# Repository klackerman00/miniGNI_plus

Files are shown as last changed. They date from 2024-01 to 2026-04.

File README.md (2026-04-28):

# miniGNI+ - An update to the original miniGNI 
Welcome to the miniGNI+, an extension of the original [miniature giant nuclei impactor (mini-GNI)](https://github.com/nugentlab/miniGNI) created at the University of Hawai'i by the [Nugent Lab](http://alisonnugent.com/). This instrument utilizes the same methodology as the original miniGNI with an improved design that facilitates use. Additionally, we've included an in-situ anemometer. More information on the methods of the original instrument can be found in this paper: 

> A New Instrument for Determining the Coarse-Mode Sea Salt Aerosol Size Distribution - [Taing et al., 2021](https://journals.ametsoc.org/view/journals/atot/38/11/JTECH-D-20-0197.1.xml)

while the microscope methods are explained in this paper: 

> The Giant Nucleus Impactor (GNI)—A System for the Impaction and Automated Optical Sizing of Giant Aerosol Particles with Emphasis on Sea Salt. Part I: Basic Instrument and Algorithms - [Jensen et al., 2020](https://journals.ametsoc.org/view/journals/atot/37/9/jtechD190109.xml?rskey=7VVZ45&result=6)

Results using the observations gathered by the miniGNI V1.0 are in this corresponding paper: 

> Mechanisms controlling giant sea salt aerosol size distributions along a tropical orographic coastline - [Ackerman et al., 2023](https://acp.copernicus.org/articles/23/13735/2023/)

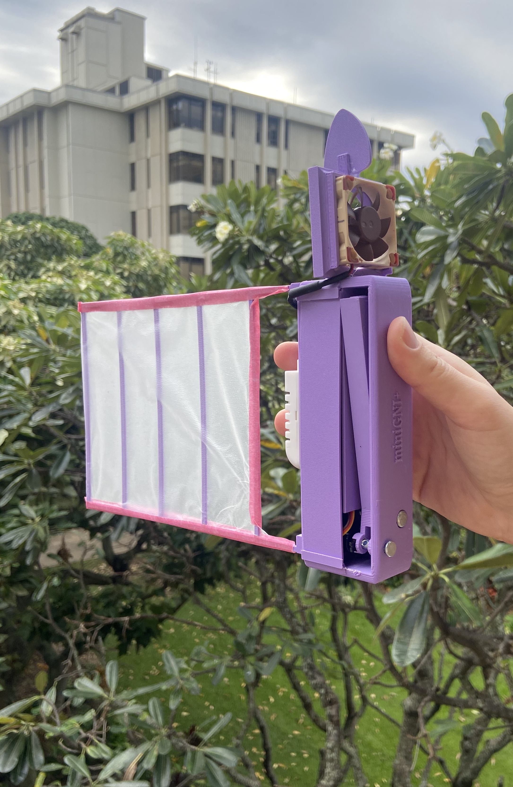
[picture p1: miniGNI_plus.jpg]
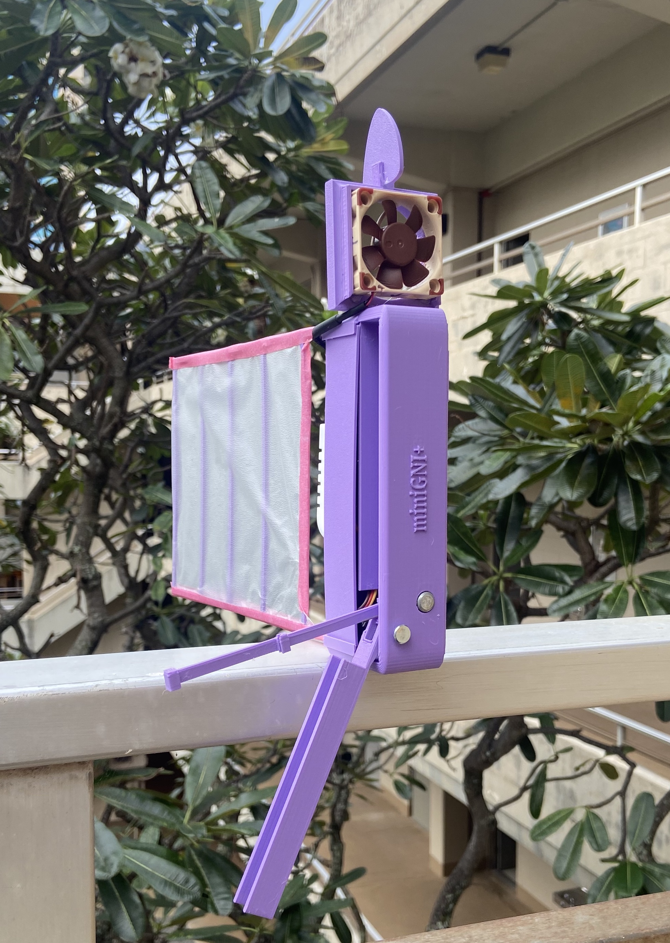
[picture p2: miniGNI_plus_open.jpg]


## Updates from the miniGNIv1.0 to the miniGNI+  
### The Door  
The door was removed from the miniGNIv1 to the miniGNI+ and replaced with an encapsulating cover. This cover offers minimal resistance against the micro-servo motor resulting in fewer failures of the door closure system (a common issue with version 1). For over 100 collected samples, the miniGNI+ closure system has never failed. Additionally, this new closure ensures no airflow around the polycarbonate slide during transport, offering increased protection from contamination over the prior model. 

### The RH Sensor
The relative humidity sensor of miniGNIv1 utilized Adafruits DHT22/2301 sensor but has been replaced with Adafruits 2301B. The 2301B sensor is practically the same, however, utilizes an I<sup>2</sup>C interface! This results in some minor changes to the wiring. 

### Detachable Wing
The wing of the miniGNI+ clips on for easy storage of the instruments. Several STL files are included at various lengths. 

### Anemometer
The largest upgrade to the miniGNI+ is the addition of an in-situ anemometer. A computer fan has been converted to an anemometer to allow for in-situ wind measurements, rather than utilizing a ground station with a wing power law conversion to calculate wind aloft. 

# In-situ Instrumentation: 
- Temperature (+/- 0.3 &deg;C)
- Relative Humidity (+/- 2%)
- Pressure/Altimetry (+/- 1.5 Pa, ~0.3 m)
- Wind Speed (+/- 0.5 m s<sup>-1</sup>)
- Sea Salt Aerosol Size Distribution 

### Optional Add-On
- Orientation (Euler Angles)

# Assembly

Gather the parts necessary for assembly. You'll need: 

### 3D Printed Parts: 
- Body (big purple body)
- Arm (small skinny)
- Anemometer house (square with circular cutout)

### Electronics: 
- Male to male pins; at least 16 continuous pieces long (less if you want to make your life harder)
- Feather M0 RFM9x LoRA radio sensor (with lipo battery and micro-usb ports)
- Adalogger Featherwing (with micro SD and CR1220 watch battery ports)
- Relative humidity sensor (black, Adafruit AM2301B)
- Altimeter (Adafruit, MPL3115A2)
- Resistor (Digikey, 10k ohm)
- Microserver motor (Adafruit, P169)
- MicroSD card
- Computer Fan (NF-A4x10 FLX Computer Fan) - [Reference to Leeman Geophysical, LLC](https://leemangeophysicalllc.github.io/mini-GNI/fan_mods.html)
- Wire for soldering parts together
- Antenna wire (specifically cut to 8.3 cm) 

### Hardware: 
- Clevis Pin (3/16 x 5/8 inches)
- Clevis Pin #2 (3/16 x 1 inch)
- Arm Spring (McMaster Carr)
- Wire for soldering together these parts
  
# Fritzing Diagram 
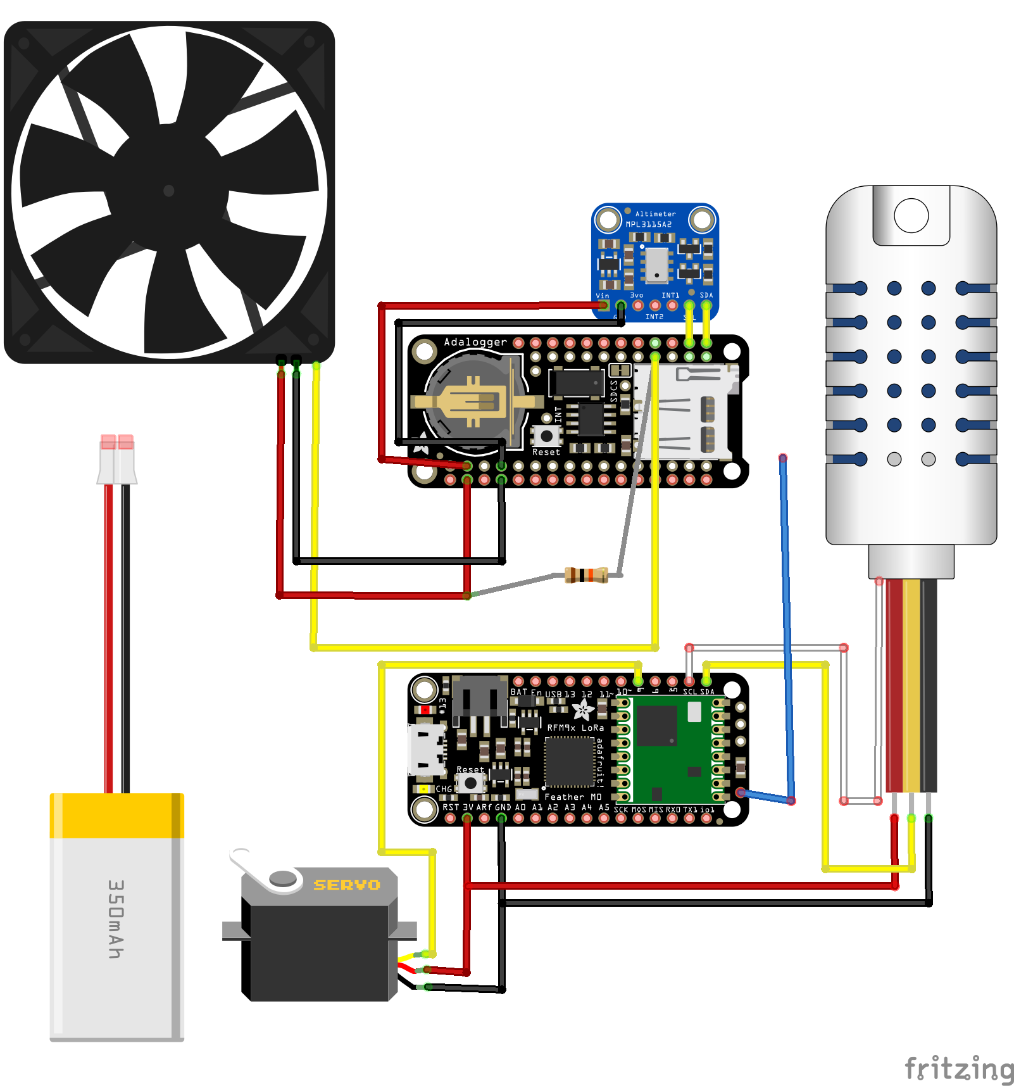
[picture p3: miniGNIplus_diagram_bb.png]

Connect the above parts using the following electrical diagram. 

# Base Station 
The base station can be made in accordance with the original base station found in [this document](https://github.com/nugentlab/miniGNI/blob/master/miniGNI_Assembly/DocumentingAssembly.docx) on the original miniGNI page. Ensure that the frequency set on your miniGNI+ and the matching base station are the same! 

# Arduino IDE Software Upload
We're currently on the V2 of the miniGNI+! Please use this updated source code that accounts for the change in relative humidity sensor from the original analog sensor to the new I2C sensor. Both code for the miniGNI and miniGNI base station are provided. 

We utilized some outdated versions of specific libraries (which we provide below). We cannot guarantee that these will work with updated libraries. 

### Libraries in use and version numbers: 
- Ethernet by Various (2.0.0)
- Firmata by Firmata (2.5.8)
- Keyboard by Arduino (1.0.2)
- LiquidCrystal by Arduino, Adafruit (1.0.7)
- Mouse by Arduino (1.0.1)
- SD by Arduino, SparkFun (1.2.4)
- Servo by Michael (1.1.7)
- Stepper by Arduino (1.1.3)
- Temboo by Temboo (1.2.1)
- Adafruit AHTX0 by Adafruit (2.0.5)
- Adafruit BNO055 by Adafruit (1.4.3)
- Adafruit BusIO by Adafruit (1.7.2)
- Adafruit Circuit Playground by Adafruit (1.10.4)
- Adafruit GFX Library by Adafruit (1.10.6)
- Adafruit ILI9341 by Adafruit (1.5.6)
- Adafruit MPL3115A2 by Adafruit (1.2.1)
- Adafruit STMPE610 by Adafruit (1.1.3)
- Adafruit TouchScreen by Adafruit (1.1.1)
- Adafruit Unified Sensor by Adafruit (1.1.4)
- DHT sensor Library by Adafruit (1.4.1)
- FIR filter by Leeman Geophysical LLC by Adafruit (0.1.1)
- RF24 by TMRh20 (1.3.11)
- RTClib by Adafruit (1.12.5)
- RadioHead by Mike McCauley (1.112)
- TinyWireM by Adafruit (1.1.0)
- Bridge by Arduino (1.7.0)
- Esplora by Arduino (1.0.4)
- GSM by Arduino (1.0.6)
- Robot Control by Arduino (1.0.4)
- Robot IR Remote by Arduino (2.0.0)
- Robot Motor by Arduino (1.0.3)
- SpacebrewYun by Julio Terra (1.0.2)
- TFT by Arduino, Adafruit (1.0.6)
- WiFI by Arduino (1.2.7)

### Specific Boards to Download: 
- Adafruit SAMD Boards (1.7.17)

This can be added by going to the Arduino IDE in the top right corner > Settings, and then adding this link to the "Additional Boards Manager URL" 
https://adafruit.github.io/arduino-board-index/package_adafruit_index.json

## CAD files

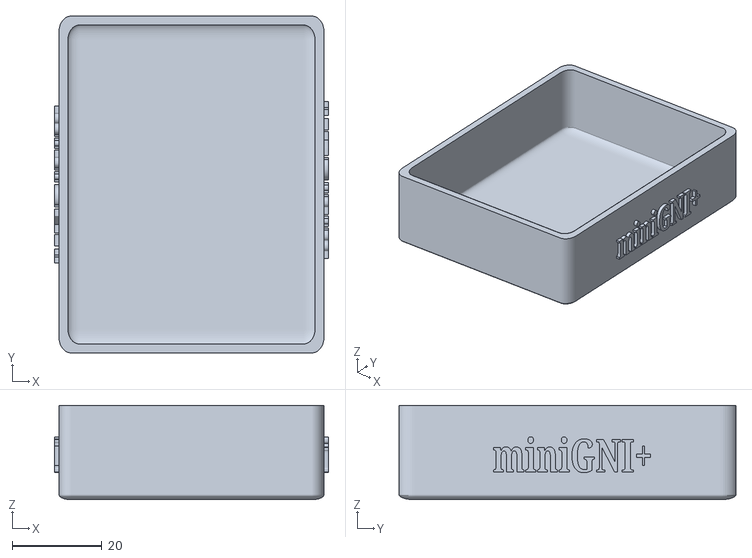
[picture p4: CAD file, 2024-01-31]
miniGNI_plus_V2/miniGNI_plus_V2_basestation_bottom.stl
61.0 x 75.0 x 21.0

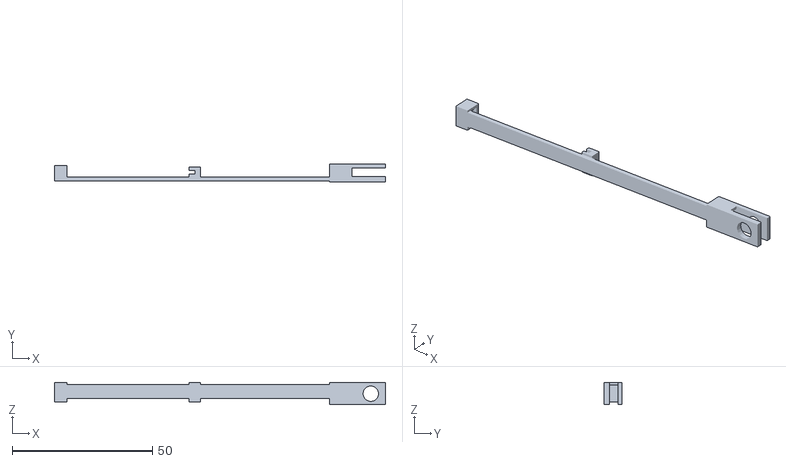
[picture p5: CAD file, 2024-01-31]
miniGNI_plus_V2/miniGNI_plus_V2_arm.stl
118.0 x 6.25 x 8.00

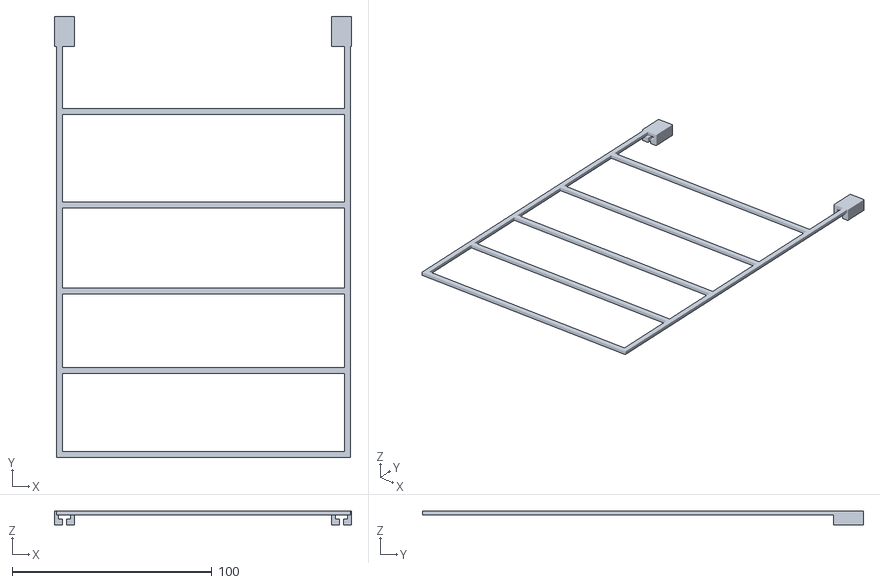
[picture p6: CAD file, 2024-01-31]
miniGNI_plus_V2/miniGNI_plus_V2_wing.stl
149.0 x 221.0 x 7.00

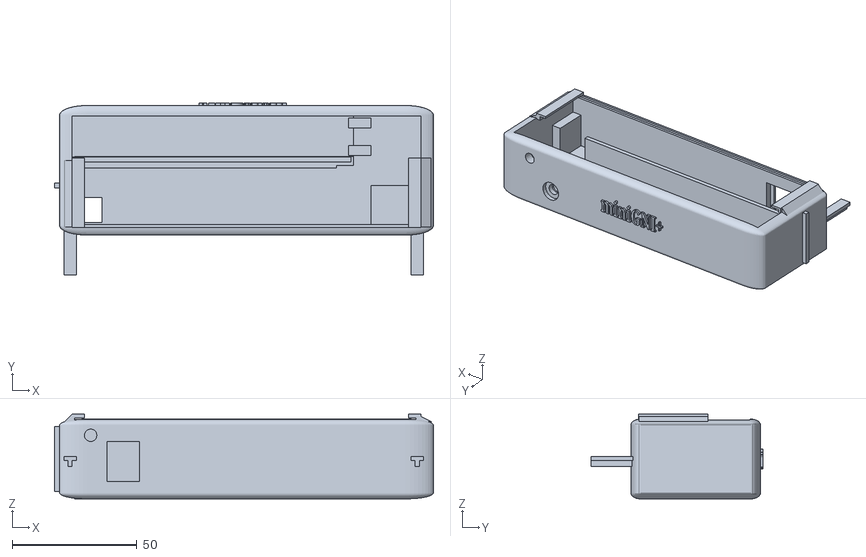
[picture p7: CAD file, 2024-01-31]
miniGNI_plus_V2/miniGNI_plus_V2_body_name.stl
152.0 x 69.0 x 34.0

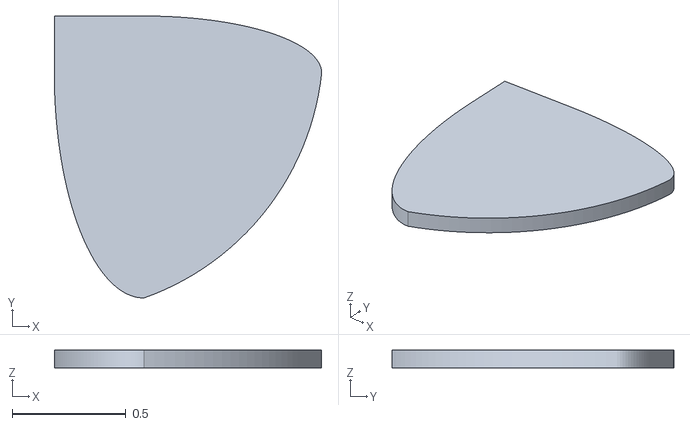
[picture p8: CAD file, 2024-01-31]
miniGNI_plus_V2/carabiner_attachment.stl
1.17 x 1.24 x 0.0787

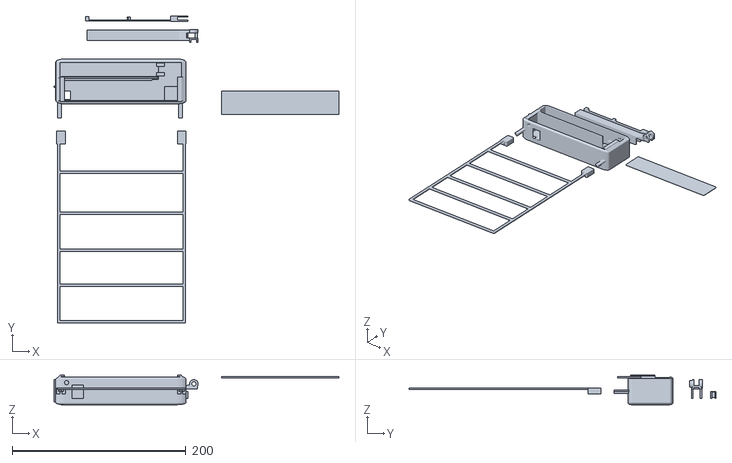
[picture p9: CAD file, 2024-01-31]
miniGNI_plus_V2/miniGNI_plus_V2_all.stl
328.0 x 353.2 x 34.0

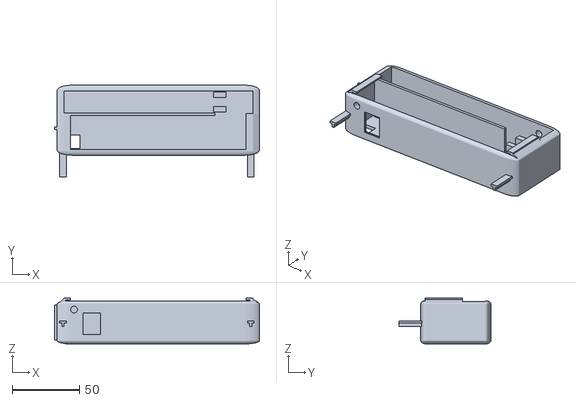
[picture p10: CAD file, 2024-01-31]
miniGNI_plus_V2/miniGNI_plus_V2_body_noname.stl
152.0 x 68.0 x 34.0

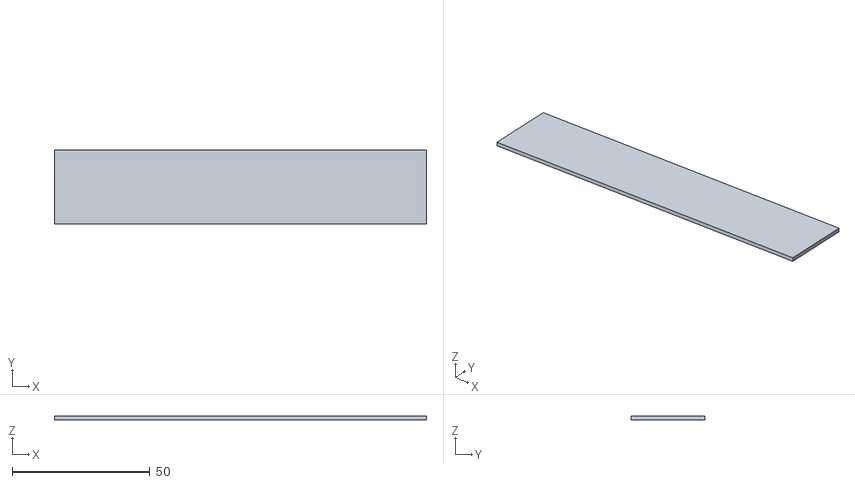
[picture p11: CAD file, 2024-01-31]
miniGNI_plus_V2/miniGNI_plus_V2_door.stl
135.0 x 27.0 x 1.50

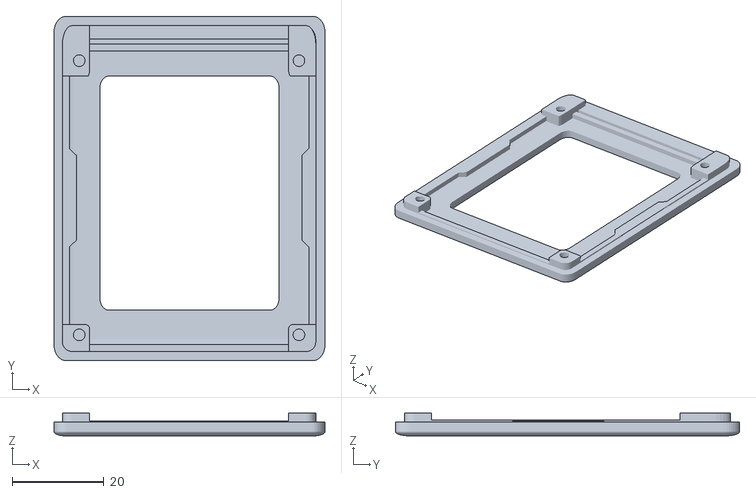
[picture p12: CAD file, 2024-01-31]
miniGNI_plus_V2/miniGNI_plus_V2_basestation_top.stl
59.0 x 75.0 x 5.00

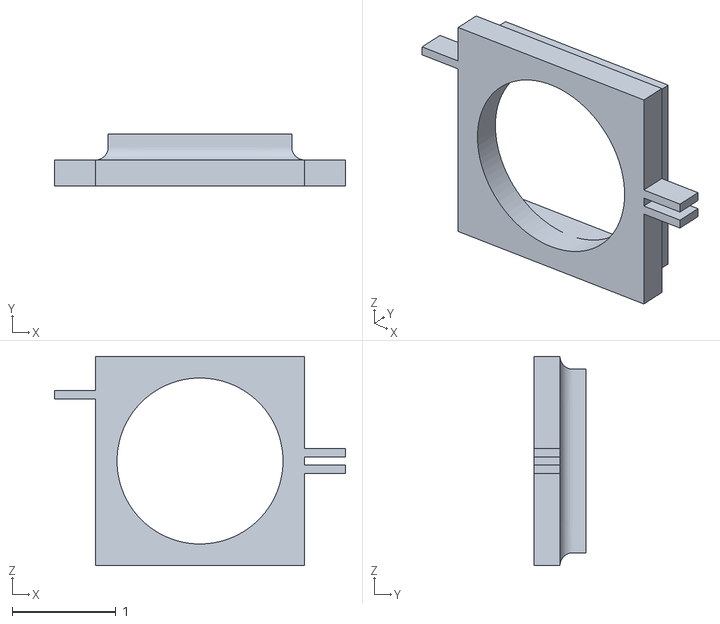
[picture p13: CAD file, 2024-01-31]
miniGNI_plus_V2/fan_mount.stl
2.81 x 0.5 x 2.02

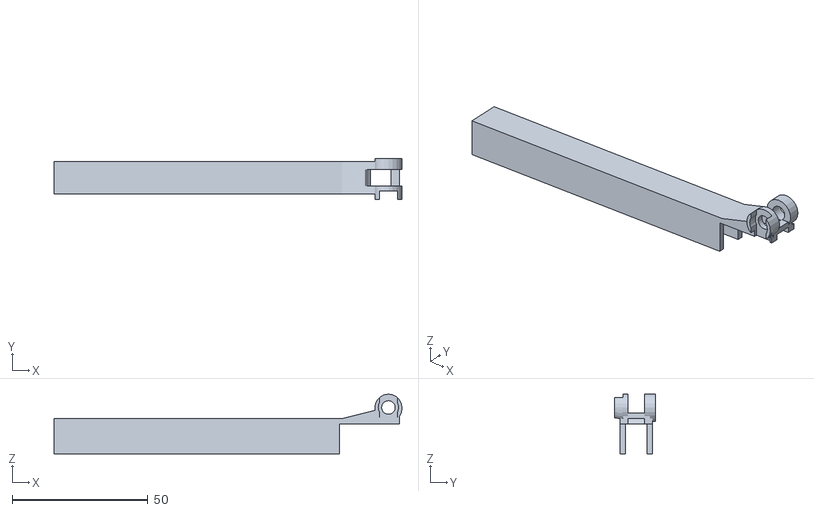
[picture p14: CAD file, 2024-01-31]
miniGNI_plus_V2/miniGNI_plus_V2_armcover.stl
128.0 x 15.0 x 22.0

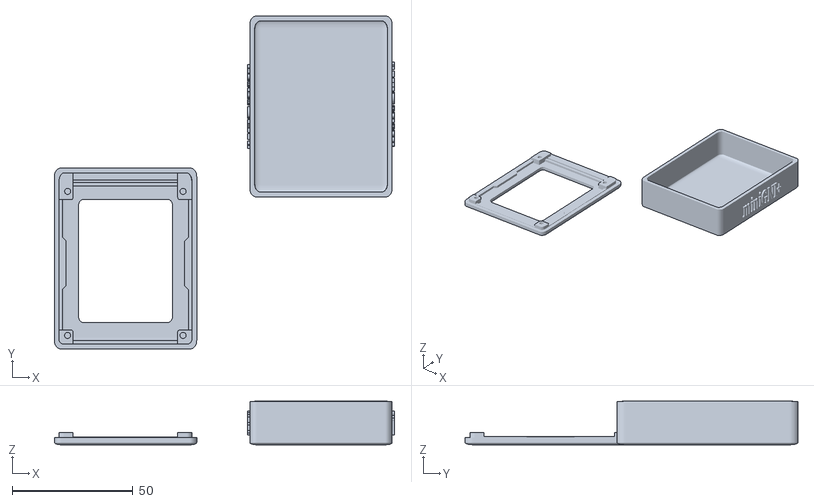
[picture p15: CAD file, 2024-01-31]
miniGNI_plus_V2/miniGNI_plus_V2_basestation.stl
141.0 x 138.0 x 18.1

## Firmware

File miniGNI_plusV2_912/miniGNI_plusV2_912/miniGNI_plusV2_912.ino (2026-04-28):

//
// Software for anemometer unit
// Version 2
// Frequency: 912 MHz
// v1  --  07/03/2019  Original file
// v2  --  08/09/2019  Added support for MPL3115A2 barometer
// v3  --  10/03/2019  Added ability for multiple anemometers to connect to one control station
// NEW VERSION CREATED FROM Anemometer and MiniGNI
// All code updated by KLA, 2023/12/28

#define USE_WIRELESS // Talk over the RFM95 LoRa Radio (adafruit id# 3178)
#define USE_SD
#define USE_BARO
#define USE_RH

#include <FIR.h>
#include <Wire.h>
#include <SPI.h>
#include <Servo.h> //KLA added 

//KLA anemometer defintions 


#define CPU_HZ 48000000
#define TIMER_PRESCALER_DIV 1024
#define SEC_WIND_AVERAGE 5 // Number of second wind average reported

//KLA miniGNI definitons
#define SERVO_PIN 9
#define SD_CHIP_SELECT 10
#define RFM95_CS 8
#define RFM95_RST 4
#define RFM95_INT 3
//#define DHTPIN 5 //KLA added this from miniGNI code
// DHT PIN WAS CHANGED BECUASE IT WAS THE SAME PIN AS THE ANEMOMETER 

//***** KLA code from miniGNI that's replaced with other functions potentially

//radio 
#ifdef USE_WIRELESS
  #include <RH_RF95.h>
  #define RF95_FREQ 912.0 //KLA change this depending on miniGNI number
  RH_RF95 rf95(RFM95_CS, RFM95_INT);
  int16_t packetnum = 0;  // packet counter, we increment per xmission
#endif
// #ifdef 
//   #include <RH_RF95.h>
//   #define RF95_FREQ 915.0 //change this depending on what mini-GNI + control station pair
//   RH_RF95 rf95(RFM95_CS, RFM95_INT);
//   int16_t packetnum = 0;  // packet counter, we increment per xmission
// #endif

//temperature humidity sensor 
// #ifdef USE_DHT
//   #include "DHT.h"
//   #define DHTTYPE DHT22
//   DHT dht(DHTPIN, DHTTYPE);
// #endif
// KLA original code from miniGNI
#ifdef USE_RH
  #include <Adafruit_AHTX0.h> //KLA added 25-06-09
  Adafruit_AHTX0 aht;
#endif

// barometer
//Adafruit_MPL3115A2 baro = Adafruit_MPL3115A2();
//KLA miniGNI code below, coded out
#ifdef USE_BARO
 #include <Adafruit_MPL3115A2.h>
 Adafruit_MPL3115A2 baro = Adafruit_MPL3115A2();
#endif

// SD CARD
#ifdef USE_SD
  #include <SD.h>
  #include "RTClib.h"
  RTC_PCF8523 rtc;
  File logfile;
#endif

//// servo motor position
//Servo myservo;
//int pos = 0;            // variable to store the servo position
//bool door_status = 0;   // 0:closed, 1:open

Servo myservo;
int pos = 0;            // variable to store the servo position
bool door_status = 0;   // 0:closed, 1:open


// Calibration constants for the anemometer
const float anemometer_calibration_coeff_a = 0;
const float anemometer_calibration_coeff_b = 0.02468637;
const float anemometer_calibration_coeff_c = 1.818727;

// Function prototypes
void TC5_Handler(void);
bool tcIsSyncing();
void tcStartCounter();
void tcReset();
void tcDisable();
void tcConfigure(int);
void isr_pin_rising();

// Make an instance of the FIR filter. In this case it will be
// an N point moving average
FIR<float, SEC_WIND_AVERAGE> fir;

char logfile_name[13];
uint32_t rising_counter = 0; // Counts the number of rising pulses
int filtered_frequency; // FIR filtered anemometer frequency



void send_windspeed_on_lora(int windspeed, int altitude)
{
  // Select LoRa
  digitalWrite(SD_CHIP_SELECT, HIGH);
  digitalWrite(RFM95_CS, LOW);
  
  // Send the scaled windspeed (windspeed * 10) via the LoRA radio
  char buffer[12] = "";
  sprintf(buffer, "%06d,%04d\r\n", altitude, windspeed);
  Serial.println(buffer);
  rf95.send((uint8_t *)buffer, 12);
  delay(10);
  rf95.waitPacketSent();

  // De-select LoRa
  digitalWrite(RFM95_CS, HIGH);
  digitalWrite(SD_CHIP_SELECT, LOW);
}

void get_log_file_name(char *filename)
{
  /*
  Format is YYMMDDHH.DAT
  YY  - Year
  MM - Month
  DD - Day
  HH  - Hour
  */

  DateTime now = rtc.now();

  strcpy(filename, "00000000.TXT");

  // Set the Year
  filename[0] = '0' + (now.year() / 10) % 10;
  filename[1] = '0' + now.year() % 10;

  // Set the Month
  filename[2] = '0' + (now.month() / 10) % 10;
  filename[3] = '0' + now.month() % 10;

  // Set the Day
  filename[4] = '0' + (now.day() / 10) % 10;
  filename[5] = '0' + now.day() % 10;

  // Set the hour
  filename[6] = '0' + (now.hour() / 10) % 10;
  filename[7] = '0' + now.hour() % 10;
}


bool check_and_initialize_file(char *fname)
{
  /*
   * Check to see if the filename already exists on the SD card. If not, create
   * it and write the header.
   */
   if (!SD.exists(fname)){
     logfile = SD.open(fname, FILE_WRITE);
     if (!logfile)
     {
       Serial.println("Cannot open/create log file.");
     }

     logfile.write("mini-GNI Anemometer Log\r\n");
     logfile.write("Anemometer calibration coefficients: ");
     char buffer[100] = "";
     sprintf(buffer, "a=%f\tb=%f\tc=%f\r\n");
     logfile.write(buffer);
     logfile.close();
   }
   return 0;
}




float frequency_to_windspeed(float a, float b, float c, uint32_t frequency)
{
  /*
   * This function turns the frequency into the windspeed using the
   * calibration coefficients for the given sensor. Currently supports
   * up to quadratic calibration curves.
   */
   if (frequency == 0)
   {
    return 0;
   }
  return a * frequency * frequency + b * frequency + c;
}



void setup()
{
  // Setup serial
  Serial.begin(115200);
  String setup_error = "NONE";
  pinMode(SERVO_PIN, OUTPUT);

  // Serial.begin(115200);
  // delay(1000);
  // Serial.println("Mini-GNIv2 + Anemometer");
  #ifdef USE_RH
    if (!aht.begin()){
      while (1) delay(10);}
  #endif  

  #ifdef USE_WIRELESS
    pinMode(RFM95_RST, OUTPUT);
    digitalWrite(RFM95_RST, HIGH);
    digitalWrite(RFM95_RST, LOW);
    delay(10);
    digitalWrite(RFM95_RST, HIGH);
    delay(10);
    if(!rf95.init()) {
      setup_error = "RF INIT";
    }
    if (!rf95.setFrequency(RF95_FREQ)) {
      setup_error = "RF FREQ";
    }
  #endif  

  #ifdef USE_BARO
    if (! baro.begin()) {
      setup_error = "BARO INIT";
    }
  #endif
  

  // Setup FIR Filter
  float fir_coef[SEC_WIND_AVERAGE];
  memset(fir_coef, 1, sizeof(fir_coef));
  fir.setFilterCoeffs(fir_coef);

  // Setup the RTC and set the datetime if it wasnt initializaed yet
  if (! rtc.begin())
  {
    Serial.println("Cannot Start RTC");
    while (1);
  }

  if (! rtc.initialized())
  {
    Serial.println("RTC not initialized - setting to compile date/time.");
    rtc.adjust(DateTime(F(__DATE__), F(__TIME__)));
  }

  // Setup interrupts and timer for anemometer measurement
  attachInterrupt(digitalPinToInterrupt(6), isr_pin_rising, RISING);
  tcConfigure(1024); //configure the timer to run at 1 Hertz (1024 counts)
  tcStartCounter(); //starts the timer

  #ifdef USE_SD
    if ( !rtc.initialized()) {
      Serial.println("RTC is NOT running! Setting now");
      rtc.adjust(DateTime(F(__DATE__), F(__TIME__))); //sets the RTC to the date & time this sketch was compiled
    }
    if (!SD.begin(SD_CHIP_SELECT)) {
      Serial.println("Card init. failed!");
    }
   
    get_log_file_name(logfile_name);
    logfile = SD.open(logfile_name, FILE_WRITE);
    logfile.print("Datetime,Frequency,Windspeed,Altitude,TemperatureC,Pressure,RelativeHum,TempDH,DoorStatus\r\n");
    //logfile.print("Timestamp\tHz\tm/s\r\n");
    logfile.close();
  #endif  

  myservo.attach(SERVO_PIN);
  myservo.write(0); //start closed!
  delay(2000); //wait for the movement
  myservo.detach();

  // Open up the logfile for this datetime and write header
 
}




// int lenMicroSecondsOfPeriod = 20 * 1000; // 20 milliseconds (ms)
// int closedPosition = 1.0 * 1000; // 1.0 ms is 0 degrees
// int openPosition = 2.0 * 1000; // 2.0 ms is 180 degrees





void loop()
{
  delay(1000);
  // Main loop:
  // * Get the measured filtered anemometer frequency.
  // * Calibrate frequency to physical units.
  // * Send the data over serial and log to file.
  // * Every 30 packets, send one via LoRA.

  //KLA from miniGNI - establishing open and close commands 
  static int radio_message_counter = 30;

  char open_command[20];
  char close_command[20];

  sprintf(open_command, "OPEN %02d",1);
  sprintf(close_command, "CLOSE %02d",1);


  // Get the measured filtered anemometer frequency.
  int anemometer_frequency = filtered_frequency;
  DateTime now = rtc.now();

  // Calibrate frequency to physical units.
  float anemometer_windspeed = frequency_to_windspeed(anemometer_calibration_coeff_a,
                                                     anemometer_calibration_coeff_b,
                                                     anemometer_calibration_coeff_c,
                                                     filtered_frequency);
  int windspeed_int = 0;
  windspeed_int = round(100*anemometer_windspeed);
  
  // read in altitude, temperature, pressure from barometer
  int altm_int = 0;
  int tempC_int = 0;
  int presP_int = 0;
  int rhDH_int = 0; //KLA
  int tempDH_int = 0; //KLA
  int wind_send = 0;

  #ifdef USE_BARO
    float altm  = baro.getAltitude();
    float tempC = baro.getTemperature();
    float presP = baro.getPressure();
    altm_int  = round(100*altm);
    tempC_int = round(100*tempC);
    presP_int = round(100*presP);
  #endif
  
  #ifdef USE_RH
    sensors_event_t humidity, temp;
    aht.getEvent(&humidity, &temp); // Read both humidity and temperature from AHT

    float rhDH = humidity.relative_humidity;
    float tempDH = temp.temperature;
    rhDH_int = round(100*rhDH);
    tempDH_int = round(100*tempDH);
  #endif

  Serial.print("Temp: ");
  Serial.println(temp.temperature);
  Serial.print("RH: ");
  Serial.println(humidity.relative_humidity);
  
  // Send data over serial and log to file.
  char message[68];
  sprintf(message, "%04d%02d%02dT%02d%02d%02d,%d,%f,%06d,%04d,%06d,%04d,%04d,%1d", now.month(), now.day(), now.year(),
          now.hour(), now.minute(), now.second(), filtered_frequency, anemometer_windspeed, altm_int, tempC_int, presP_int, rhDH_int,tempDH_int,door_status);
  
 // Write message to file
   #ifdef USE_SD
    digitalWrite(8,HIGH);
    delay(100);
    File logfile = SD.open(logfile_name, FILE_WRITE);
    logfile.println(message);
    logfile.close();
    digitalWrite(8,LOW);
    Serial.println("Transmitting..."); // Send a message to rf95_server  
    Serial.print("Sending "); 
    Serial.println(message);
    Serial.println("Sending...");
    delay(10);
    //digitalWrite(RFM95_CS, LOW); 
  #endif
  // Echo to serial terminal (optional)
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

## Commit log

2024-01-31 Adding STL files
    [carabiner_attachment.stl, fan_mount.stl, miniGNI_plus_V1_all.stl, miniGNI_plus_V1_arm.stl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]
2026-04-21 MiniGNI+ V2 STL files
    [arm_v2.3.stl, body_v2.3.stl, cover_v2.3.stl]
2026-04-21 STL Files for miniGNI+ V2
    [carabiner_attachment.stl, fan_mount.stl, miniGNI_plus_V2_all.stl, miniGNI_plus_V2_arm.stl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]
